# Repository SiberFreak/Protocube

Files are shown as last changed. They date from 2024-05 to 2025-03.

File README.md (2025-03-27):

# Protocube
Animation_Flourescent
Animation_Transmitted
A microscope built using 3D printed Cubes! Check out our paper!!! https://ojs.lib.uwo.ca/index.php/openhardware/article/view/22245

https://github.com/user-attachments/assets/49f3d98f-34b9-44ec-8753-2452c5d8e914

https://github.com/user-attachments/assets/b85a2b6f-8580-445c-ac9c-59f73a623541

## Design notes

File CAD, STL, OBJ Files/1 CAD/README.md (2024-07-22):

# CAD Files
Render Flourescent Upper
Render Transmitted Upper
A selection of CAD files from Autodesk Inventor Pro for everything from the cubes to tools used to assemble them.

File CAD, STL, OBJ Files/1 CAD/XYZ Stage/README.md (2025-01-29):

# XYZ Stage
Render_XYZ_Stage
An XYZ-Stage designed to use consumer electronics from Pimoroni and put them together into a functional, position control stage with an integrated LED. Currently no other attachments for the stage are available.

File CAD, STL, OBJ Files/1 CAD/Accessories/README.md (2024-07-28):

# Accessories
Render_Attatchments
A few different accessories allowing for external compatability or devices as well as some parts for light oclusion.

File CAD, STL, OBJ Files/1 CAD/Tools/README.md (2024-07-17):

# Tools
Render_Tools
A set of tools usefull for helping in the assembly of the cubes and baseplate, as well as for aligning the beam path.

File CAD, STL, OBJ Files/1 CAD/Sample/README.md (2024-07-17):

# Sample
Render_Sample
Am alternative fixed mount for a sample plate.

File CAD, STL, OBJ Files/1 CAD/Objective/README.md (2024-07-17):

# Objective
Render_Objective
A Pink cube designed to hold a standard microscope objective. It is placed at the appropriate distance on the z-axis for use with a stage.

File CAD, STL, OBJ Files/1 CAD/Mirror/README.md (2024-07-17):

# Mirrors
Render_Mirror_Horizontal
Render_Mirror_Vertical
Purple cubes designed to fit a rectangular mirror. The mirror’s distance and alignment are determined by three brass thread inserts heat pressed in, along with an M3 Screw contacting magnets on the mirror plate.

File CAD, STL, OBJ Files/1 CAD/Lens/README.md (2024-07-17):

# Lenses
Render_Lens_One_Inch
Render_Lens_Half_Inch
Light Blue Cubes designed to hold a standard 1” and 1/2" optical lens, the lens is fixed in place by an M4 set screw and a press fit cap for extra security. The lens is aligned positionally by two M6 set screws and a manual rail adjustment.

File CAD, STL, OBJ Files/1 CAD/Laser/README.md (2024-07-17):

# Laser
Render_Light_Source
A White cube that holds the light source and is adjustable in the same way as the lenses, but with two mounts to align and tilt the light source. It also includes covers to be enclosed once aligned.

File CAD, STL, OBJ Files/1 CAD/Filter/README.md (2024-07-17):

# Filters
Render_Filter
A few different ways of mounting filts, both to the cubes and the usb lasers.

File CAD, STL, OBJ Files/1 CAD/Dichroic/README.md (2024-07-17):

# Dichroic
Render_Dichroic
A Yellow cube designed to hold a standard 1” Dichroic. It is sized for SM1 to hold standard 1” filters via press fit.

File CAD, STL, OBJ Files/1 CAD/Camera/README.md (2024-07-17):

# Camera
Render_Camera
A Red cube designed to fit a standard size SM1 via a press fit and keep the light path enclosed.

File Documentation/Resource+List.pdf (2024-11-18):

Part | Description | Weight(g, ml) | CostPerUnit | Amount | Price | Link

Printed Parts (Cubes)

Cube V5 (Slotted) | N/A | 23.6 | $0.71 | 6 | $4.26 | Github (https://github.com/Siber18/Protocube/tree/main)
Cube V5 (Closed) | N/A | 26.94 | $0.81 | 23 | $18.63 | Github (https://github.com/Siber18/Protocube/tree/main)
Cube V5 (Mixed) | N/A | 22.11 | $0.66 | 2 | $1.32 | Github (https://github.com/Siber18/Protocube/tree/main)
Cube V5 | N/A | 18.06 | $0.54 | 2 | $1.08 | Github (https://github.com/Siber18/Protocube/tree/main)

Printed Parts (Inserts)

Dichroic Mirror Mount | N/A | 23.37 | $0.70 | 1 | $0.70 | Github (https://github.com/Siber18/Protocube/tree/main)
Filter Mount SM1 | N/A | 4.44 | $0.13 | 1 | $0.13 | Github (https://github.com/Siber18/Protocube/tree/main)
Filter Mount SM05 | N/A | 5.64 | $0.17 | 0 | $0.00 | Github (https://github.com/Siber18/Protocube/tree/main)
Half Inch Lense Holder | N/A | 4.62 | $0.14 | 1 | $0.14 | Github (https://github.com/Siber18/Protocube/tree/main)
One Inch Lense Holder | N/A | 5.86 | $0.18 | 3 | $0.54 | Github (https://github.com/Siber18/Protocube/tree/main)
One Inch Lense Holder (SM1) | N/A | 6.32 | $0.19 | 0 | $0.00 | Github (https://github.com/Siber18/Protocube/tree/main)
One Inch Lense Holder (SM05) | N/A | 4.52 | $0.14 | 0 | $0.00 | Github (https://github.com/Siber18/Protocube/tree/main)
Laser Mount (USB Laser) | N/A | 5.21 | $0.16 | 2 | $0.32 | Github (https://github.com/Siber18/Protocube/tree/main)
Laser Mount (Smaller Laser) | N/A | 4.70 | $0.14 | 0 | $0.00 | Github (https://github.com/Siber18/Protocube/tree/main)
Mirror Base Horizontal | N/A | 9.43 | $0.28 | 2 | $0.56 | Github (https://github.com/Siber18/Protocube/tree/main)
Mirror Plate Horizontal | N/A | 4.23 | $0.13 | 2 | $0.26 | Github (https://github.com/Siber18/Protocube/tree/main)
Mirror Base Vertical | N/A | 13.50 | $0.41 | 1 | $0.41 | Github (https://github.com/Siber18/Protocube/tree/main)
Mirror Plate Vertical | N/A | 3.56 | $0.11 | 1 | $0.11 | Github (https://github.com/Siber18/Protocube/tree/main)
Flashlight Mount | N/A | 14.68 | $0.44 | 1 | $0.44 | Github (https://github.com/Siber18/Protocube/tree/main)
Objective Mount | N/A | 13.12 | $0.39 | 1 | $0.39 | Github (https://github.com/Siber18/Protocube/tree/main)
Tunnel Horizontal | N/A | 21.17 | $0.64 | 1 | $0.64 | Github (https://github.com/Siber18/Protocube/tree/main)
Tunnel Vertical | N/A | 14.49 | $0.43 | 1 | $0.43 | Github (https://github.com/Siber18/Protocube/tree/main)

Printed Parts (XYZ Stage)

X Stage Body | N/A | 5.71 | $0.17 | 1 | $0.17 | Github (https://github.com/Siber18/Protocube/tree/main)
XStage Clamp | N/A | 1.29 | $0.04 | 1 | $0.04 | Github (https://github.com/Siber18/Protocube/tree/main)
X Stage Motor Clamp | N/A | 0.91 | $0.03 | 1 | $0.03 | Github (https://github.com/Siber18/Protocube/tree/main)
X Stage Part | N/A | 6.86 | $0.21 | 1 | $0.21 | Github (https://github.com/Siber18/Protocube/tree/main)
Y Stage Body | N/A | 10.81 | $0.32 | 1 | $0.32 | Github (https://github.com/Siber18/Protocube/tree/main)
Y Stage Motor Clamp | N/A | 1.2 | $0.04 | 1 | $0.04 | Github (https://github.com/Siber18/Protocube/tree/main)
Y Stage Part | N/A | 3.02 | $0.09 | 1 | $0.09 | Github (https://github.com/Siber18/Protocube/tree/main)
Z Stage Body | N/A | 63.58 | $1.91 | 1 | $1.91 | Github (https://github.com/Siber18/Protocube/tree/main)
Z Stage Electrical Cover | N/A | 4.07 | $0.12 | 1 | $0.12 | Github (https://github.com/Siber18/Protocube/tree/main)
Z Stage LED Mount | N/A | 1.13 | $0.03 | 1 | $0.03 | Github (https://github.com/Siber18/Protocube/tree/main)
Z Stage Motor Clamp | N/A | 1.08 | $0.03 | 1 | $0.03 | Github (https://github.com/Siber18/Protocube/tree/main)
Z Stage Part | N/A | 20.34 | $0.61 | 1 | $0.61 | Github (https://github.com/Siber18/Protocube/tree/main)
Joystick Lower Mount | N/A | 3.72 | $0.41 | 1 | $0.41 | Github (https://github.com/Siber18/Protocube/tree/main)
Joystick Upper Mount | N/A | 2.58 | $0.08 | 1 | $0.08 | Github (https://github.com/Siber18/Protocube/tree/main)

Printed Parts (Tools)

Baseplate Magnet Press | N/A | 32.62 | $0.98 | 1 | $0.98 | Github (https://github.com/Siber18/Protocube/tree/main)
Bottom Cube Press | N/A | 6.01 | $0.18 | 1 | $0.18 | Github (https://github.com/Siber18/Protocube/tree/main)
Top Cube Press | N/A | 6.01 | $0.18 | 1 | $0.18 | Github (https://github.com/Siber18/Protocube/tree/main)
Laser Alignment Tool | N/A | 3.27 | $0.10 | 25 | $2.50 | Github (https://github.com/Siber18/Protocube/tree/main)

Parts List (McMaster)

Multipurpose 304 Stainless Steel Rod | 3mm x 3ft | N/A | $9.42 | 1 | $9.42 | https://www.mcmaster.com/1272T33-1272T12/
Alloy Steel Low-Profile Socket Head Screw | M3 x 0.5 mm Thread, 12 mm Long 25ct | N/A | $7.85 | 1 | $7.85 | https://www.mcmaster.com/93070A070/
Black-Oxide Alloy Steel Socket Head Screw | M3 x 0.5 mm Thread, 8 mm Long, 100ct | N/A | $9.22 | 1 | $9.22 | https://www.mcmaster.com/91290A113/

Parts List (Thorlabs)

Optical Adhesive | Bonding Glass to Plastic | N/A | $40.70 | 1 | $40.70 | https://www.thorlabs.com/thorproduct.cfm?partnumber=NOA68
F30 1/2" Lense | 1/2" Lense | N/A | $60.59 | 1 | $60.59 | https://www.thorlabs.com/thorproduct.cfm?partnumber=AC127-030-A
F200 1" Lense | 1" Lense | N/A | $89.10 | 3 | $267.30 | https://www.thorlabs.com/thorproduct.cfm?partnumber=AC254-200-A
M4 x 5mm Setscrew | 50ct | N/A | $5.90 | 1 | $5.90 | https://www.thorlabs.com/thorproduct.cfm?partnumber=SS4MS5
M6 x 12mm Secrew | 25ct | N/A | $6.43 | 1 | $6.43 | https://www.thorlabs.com/thorproduct.cfm?partnumber=SS6MS10
M6 x 16mm Setscrew | 25ct | N/A | $6.97 | 1 | $6.97 | https://www.thorlabs.com/thorproduct.cfm?partnumber=SS6MS16

Parts List (Amazon)

Magnets 4mm | 200ct | N/A | $9.99 | 5 | $49.95 | https://a.co/d/f4sNGOT
Magnets 5mm | 150ct | N/A | $9.99 | 1 | $9.99 | https://a.co/d/0iCdR7lo
M3 x 0.5-Pitch Length Coupling Nuts | 8mm | N/A | $7.39 | 1 | $7.39 | https://a.co/d/6JjM6d4
Knurled Threaded Insert | M3 x 5mm L x 4mm OD, 100ct | N/A | $8.50 | 1 | $8.50 | https://a.co/d/bxMPw1L
Motor Gearboxes | DC 6V Gear Motor | N/A | $8.61 | 3 | $25.83 | https://a.co/d/5GOWpqV
Mini USB Cable | For Camera | N/A | $5.99 | 1 | $5.99 | https://a.co/d/7T3tGII
Super Glue | You will need it | N/A | $9.99 | 1 | $9.99 | https://a.co/d/7T3tGII
Hot Glue Gun | You will need it | N/A | $18.97 | 1 | $18.97 | https://a.co/d/0bAOghhe
USB-C Cables x 2 | For XYZ Stage | N/A | $5.99 | 1 | $5.99 | https://a.co/d/i5DBRwO
Stainless Steel Rods | For XYZ Stage | N/A | $7.99 | 0.25 | $2.00 | https://a.co/d/hvkBlIS

Parts List (Adafruit)

Gamepad | Mini I2C Gamepad with seesaw - STEMMA QT / Qwiic | N/A | $7.50 | 1 | $7.50 | https://www.adafruit.com/product/5743
Adafruit LED Sequins | Warm White | N/A | $3.95 | 1 | $3.95 | https://www.adafruit.com/product/1758

Parts List (DigiKey)

STEMMA QT/QWIIC CABLE | 400mm | N/A | $1.50 | 1 | $1.50 | https://www.digikey.com/en/products/detail/adafruit-industries-llc/5385/16546436
QUAD MOTOR CONTROLLER | MOTOR 2040 | N/A | $24.60 | 1 | $24.60 | https://www.digikey.com/en/products/detail/pimoroni-ltd/PIM618/17051430

Parts List (Pimoroni)

JST-SH Cables x 4 | 300mm | N/A | $4.90 | 1 | $4.90 | https://shop.pimoroni.com/products/jst-sh-cable-6-pin?variant=39292536488019
Encoder Kits | Micro Metal Motor Encoder (MMME) (pack of 2) | N/A | $9.42 | 1 | $9.42 | https://shop.pimoroni.com/products/micro-metal-motor-encoder?variant=39888423321683
Encoder Kits (Sideways) | Micro Metal Motor Encoder (MMME) (pack of 2) | N/A | $9.42 | 1 | $9.42 | https://shop.pimoroni.com/products/micro-metal-motor-encoder?variant=39888423354451
Motors | Micro Metal Gearmotor (Extended back shaft) – 50:1 | N/A | $4.82 | 3 | $14.46 | https://shop.pimoroni.com/products/micro-metal-gearmotor-extended-back-shaft?variant=3073681025
QUAD MOTOR CONTROLLER | MOTOR 2040 | N/A | $30.00 | 1 | $30.00 | https://shop.pimoroni.com/products/motor-2040?variant=39884997853267

Parts List (Misc)

Barrel Jack Switch | For any other lasers | N/A | $2.75 | 1 | $2.75 | https://www.sparkfun.com/products/11705
Heat Set Insert Kit | M3 Heat Inserts | N/A | $9.89 | 1 | $9.89 | https://west3d.com/products/heat-insert-tool-kit
White Acrylic (Standard) | Opaque, Glossy, Masked, Cast, 1/8" | N/A | $18.50 | 1 | $18.50 | https://shop.glowforge.com/products/white-acrylic-cast-opaque-glossy?variant=39434530783330
Laptop | Gateway 11.6" Ultra Slim Notebook | N/A | $89.00 | 1 | $89.00 | Gateway 11.6" Ultra Slim Notebook, HD, Intel® Celeron®, Dual Core, 64GB Storage, 4GB RAM, Mini HDMI, 1.0MP Webcam, Windows 10 S (https://www.walmart.com/ip/Gateway-11-6-Ultra-Slim-Notebook-HD-Intel-Celeron-Dual-Core-64GB-Storage-4GB-RAM-Mini-HDMI-1-0MP-Webcam-Windows-10-S-Microsoft-365-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)
Prusament PLA | One for Each Color + 3 Blacks | 1000g | $30.00 | 12 | $360.00 | https://www.prusa3d.com/category/prusament-pla/
Bambu Labs PLA-CF | 1kg | 1000g | $34.99 | 1 | $34.99 | https://us.store.bambulab.com/products/pla-cf?variant=41003202248840
Bambu Lab A1 Printer Bundle | Recommended Printer | N/A | $1,449.00 | 1 | $1,449.00 | https://us.store.bambulab.com/collections/3d-printer/products/a1

Mirrors

Plane Mirror General Purpose | 40x25x3mm | N/A | 20.57 | 3 | $61.71 | https://www.knightoptical.com/stock/plane-mirror-f-s-general-purpose-40x25x3mmthk-enhanced-aluminium-visible-use.html

Lasers (Choose One)

Red Laser | 650nm | N/A | $9.98 | 1 | $9.98 | https://a.co/d/3TRZW0U
Blue Laser | 405nm | N/A | $17.98 | 1 | $17.98 | https://a.co/d/7nuj360
Green Laser | 532nm | N/A | $9.98 | 1 | $9.98 | https://a.co/d/a5kr8Kf

Cameras (Choose One)

DMK 22BUC03

The Imaging Source “One for all” camera, USB 2.0, 1/3“ CMOS, monochrome, max resolution 744x480, ROI to increase speed, global shutter, trigger in, digital out, C/CS-mount (Without lens and cables)

N/A | $206.00 | 1 | $206.00 | https://dl-gui.theimagingsource.com/en_US/0ea79de3-100f-510e-8601-2ba7061b001e/

DMK 42BUC03

The Imaging Source “One for all” camera, USB 2.0, 1/3“ CMOS, monochrome, 1280x960 pixel, global shutter, trigger in, digital out, C/CS-mount, WITHOUT lens and cables

N/A | $229.00 | 1 | $229.00 | https://www.theimagingsource.com/en-us/product/industrial/2u/dmk42buc03/

Objectives (Choose One)

20x Microscope Objective Lens | CCIS EC Plan 20x Strain Free Microscope Objective Lens | N/A | $317.00 | 1 | $317.00 | https://www.motic-microscope.com/p-763-ccis-ec-plan-20x-strain-free-microscope-objective-lens.aspx
40x Microscope Objective Lens | CCIS EC Plan 40x Strain Free Microscope Objective Lens | N/A | $414.00 | 1 | $414.00 | https://www.motic-microscope.com/p-1846-ccis-ec-plan-40x-strain-free-microscope-objective-lens.aspx

Dichroics & Filters (Choose One)

Custom_405LaserSetZET405/10xT4 | Chroma ID: CS451075, Containing zet405/10x, T425LPXR-UF1 and ET460/50m,25mm diameter excitation/clean-up and barrier/emissionfilters, 25.5x36x1mm thick dichroic mirror | N/A | $825.00 | 1 | $825.00 | N/A

Custom_532LaserSetZET532/10xZT

Chroma ID: CS451193, Containing zet532/10x, zt532rdc-UF1 and ET575/50m,25mm diameter excitation/clean-up and barrier/emissionfilters, 25.5x36x1mm thick dichroic mirror

N/A | $825.00 | 1 | $825.00 | N/A

Custom_640LaserSetZET640/20xZT

Chroma ID: CS451194, Containing zet640/20x, zt640rdc-UF1 and ET690/50m,25mm diameter excitation/clean-up and barrier/emissionfilters, 25.5x36x1mm thick dichroic mirror

N/A | $825.00 | 1 | $825.00 | N/A

## Total

$2,765.84

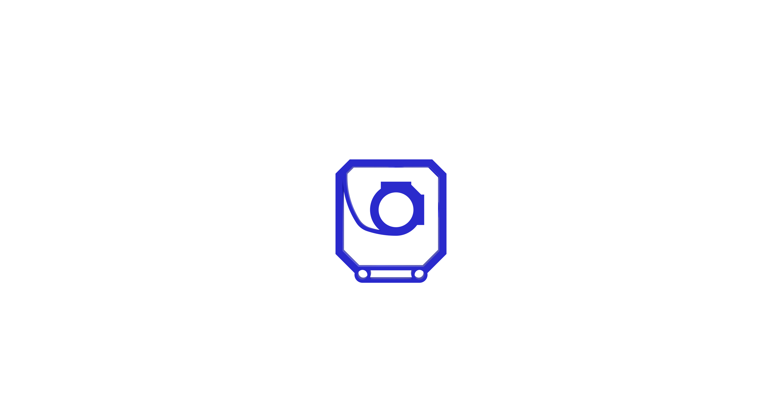
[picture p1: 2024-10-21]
Resources/Renders/Basic_Renders/Render_Lens_Mount_Half_Inch.png

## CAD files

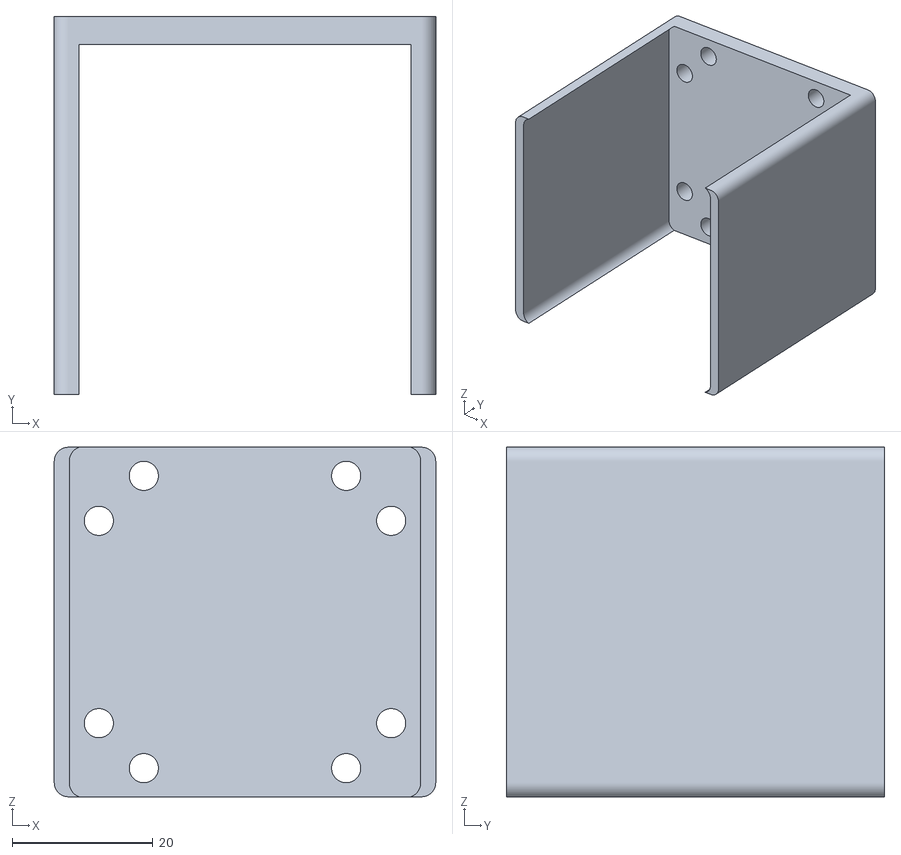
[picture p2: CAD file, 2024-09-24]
CAD, STL, OBJ Files/2 STL/V5_Outer Cover Full_61.stl
54.3 x 53.8 x 49.8

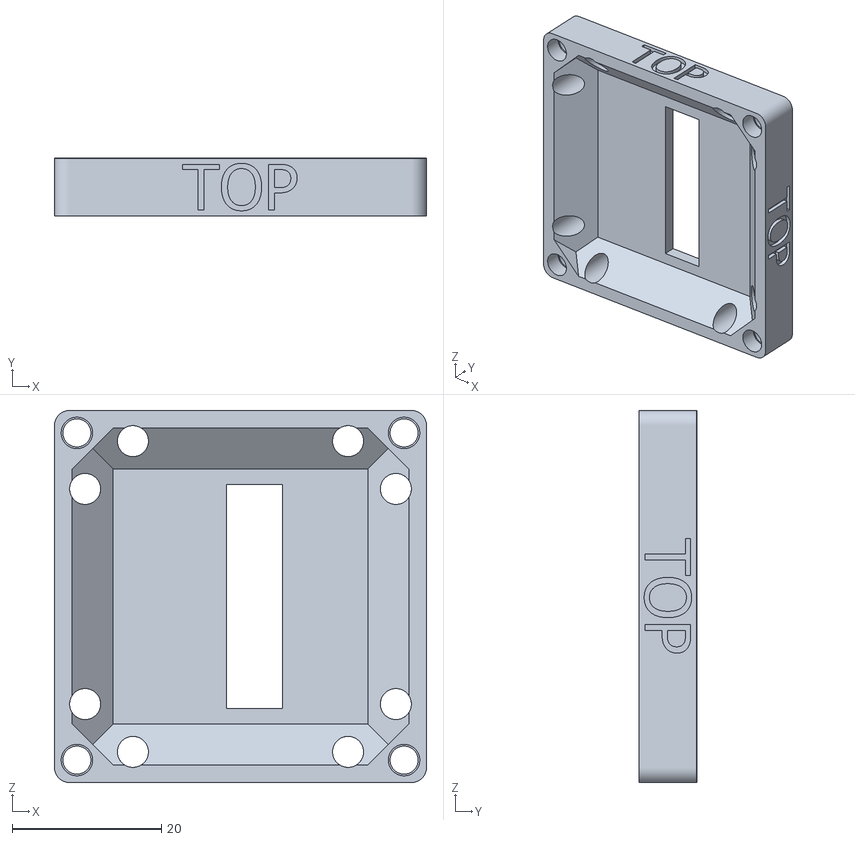
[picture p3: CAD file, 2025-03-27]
CAD, STL, OBJ Files/2 STL/V5_Cube 1x1 Top V5 Closed Slotted_5.stl
49.8 x 7.70 x 49.8

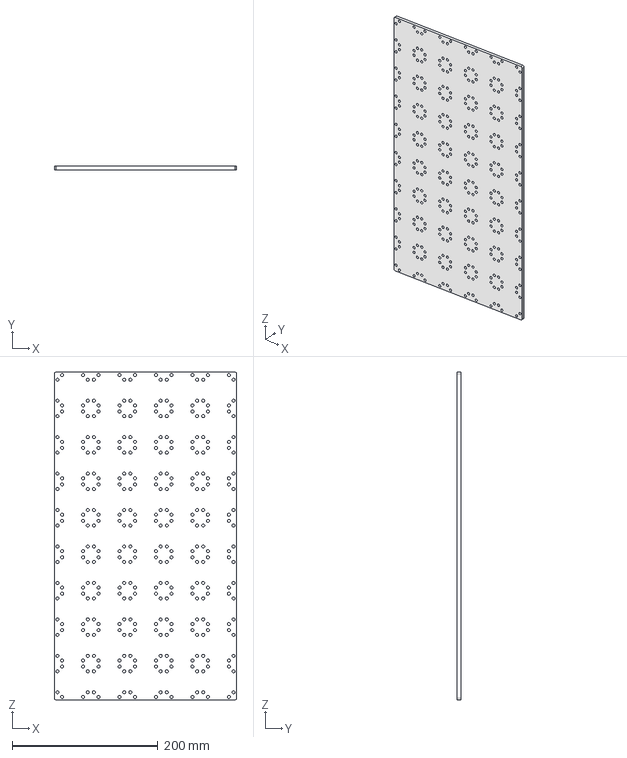
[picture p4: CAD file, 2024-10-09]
CAD, STL, OBJ Files/4 STEP/Baseplate 9x5 V5.stp
250.0 x 5.00 x 450.0 mm

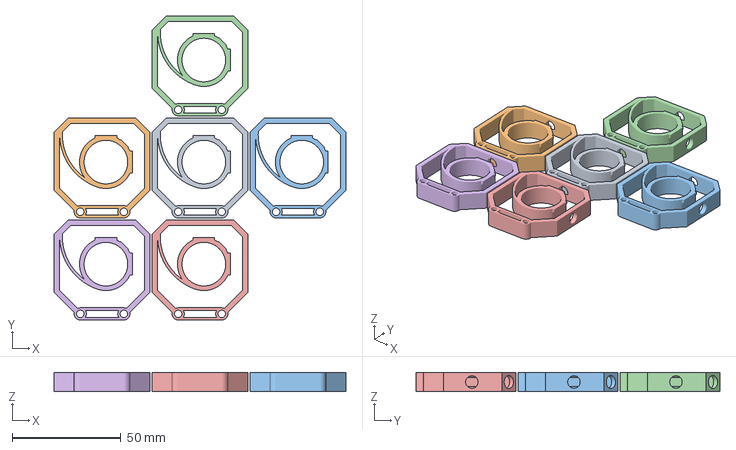
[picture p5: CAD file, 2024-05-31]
Resources/Slicer Files/Laser Holders.3mf
133.8 x 139.5 x 8.75 mm
Cube 1x1 V5_Laser Holder (USB Laser)_22.stl x 6

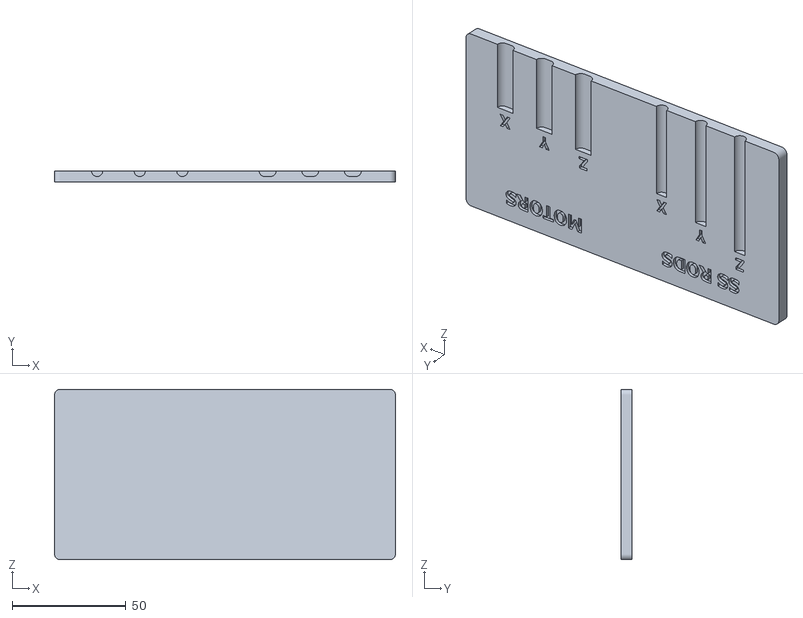
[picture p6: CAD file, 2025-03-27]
CAD, STL, OBJ Files/2 STL/V5_Rod_Motor_Lengths_15.stl
150.0 x 5.00 x 75.0

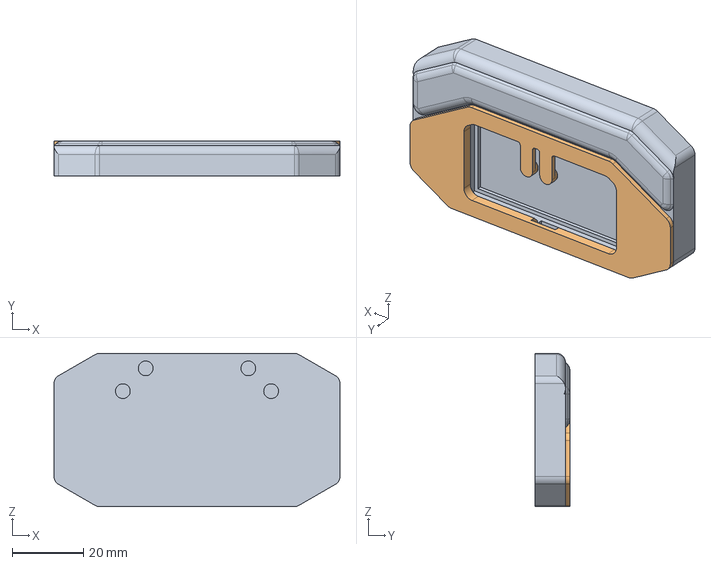
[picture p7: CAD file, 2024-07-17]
CAD, STL, OBJ Files/4 STEP/Gamepad Enclosure.stp
80.2 x 9.75 x 43.0 mm
Joystick Bottom
Joystick Top

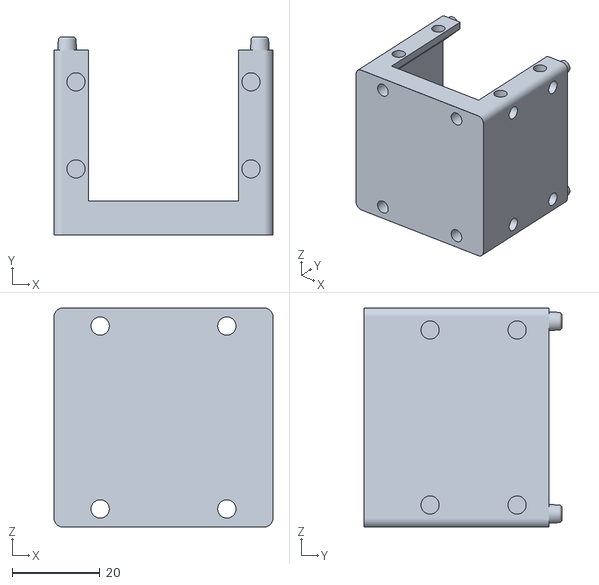
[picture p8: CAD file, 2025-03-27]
CAD, STL, OBJ Files/2 STL/V5_Cube 1x1 Bottom V5 Closed_4.stl
49.8 x 45.0 x 49.8

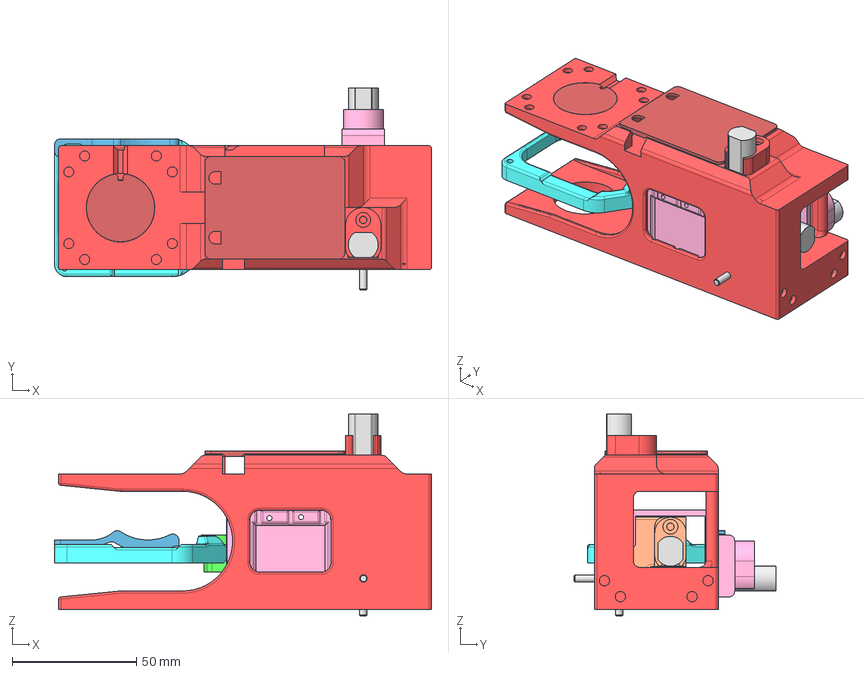
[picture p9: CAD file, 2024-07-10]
CAD, STL, OBJ Files/4 STEP/XYZ Stage V5.stp
151.4 x 81.0 x 81.0 mm
DC Motor x 3
Z Stage Body New
Z Stage Part V5
Z Stage LED Mount V5
Z Stage Electrical Cover
Z Stage Motor Clamp V5
Y Stage Body v5
Y Stage Part V5
Y Stage Motor Clamp V5
X Stage Body V5
X Stage Part V5
X Stage Clamp V5
X Stage Motor Clamp V5

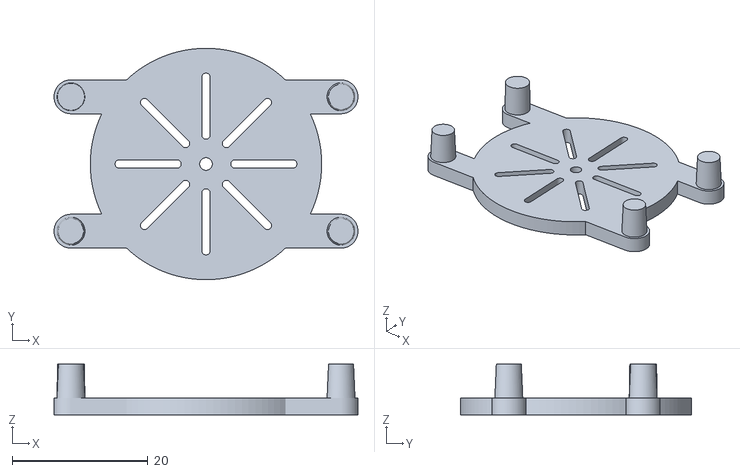
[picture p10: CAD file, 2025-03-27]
CAD, STL, OBJ Files/2 STL/V5_Laser Alignment Tool V1_9.stl
44.8 x 34.1 x 7.50

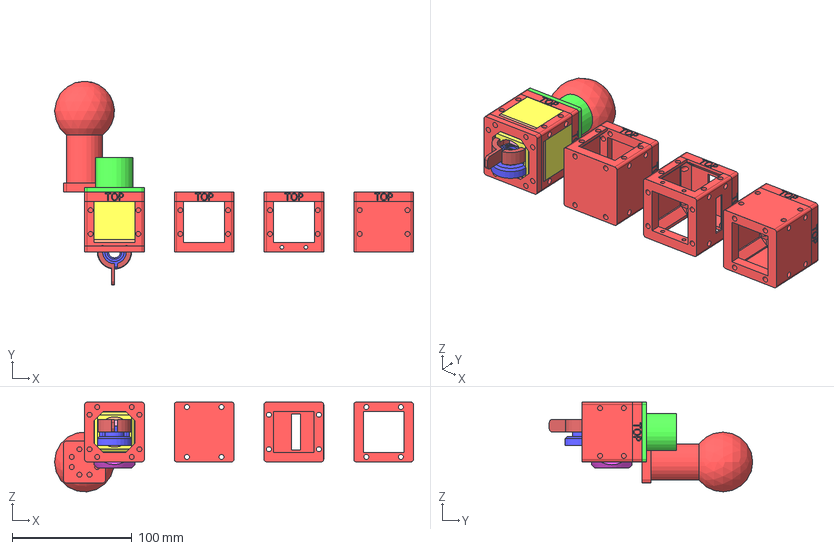
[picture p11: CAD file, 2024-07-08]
CAD, STL, OBJ Files/4 STEP/Cube 1x1 V5.stp
299.3 x 169.7 x 74.8 mm
Cube 1x1 Top V5 x 2
Cube 1x1 Bottom V5
Cube 1x1 Top V5 Closed
Cube 1x1 Bottom V5 Closed
Cube 1x1 Top V5 Closed Slotted Rails
Cube 1x1 Bottom V5 Closed Slotted Rails
Cube 1x1 Bottom V5 Closed Vertical
Laser Alignment Tool V1
Laser Alignment Tool V2
Cube Press Top
Cube 1x1 V5 Bot Press
Cube 1x1 V5 Press
Laser Switch
Half Inch Lense Holder Cover (V5)
One Inch Lense Holder Cover (V5)
Half Inch Lense Holder (V5)
One Inch Lense Holder (V5)
Laser Holder (USB)
Laser Holder (Blue Laser)
SM05 Lense Holder (V5)
Special One Inch Lense Holder (V5)
Filter Mount (SM1)
Filter Mount (SM1)_1
Mirror Base
Mirror Plate
Mirror Base Horizontal
Mirror Plate Horizontal
Dichroic Mirror Mount (V2)
Camera Mount Side
Objective Mount
Filter Adapter (SM1)
Filter Adapter (SM05)
Camera Mount Top
Top Mount (SM05)
Flashlight Mount V1
Cover Side (Normal) Proto
Cover Side (Slotted) Proto

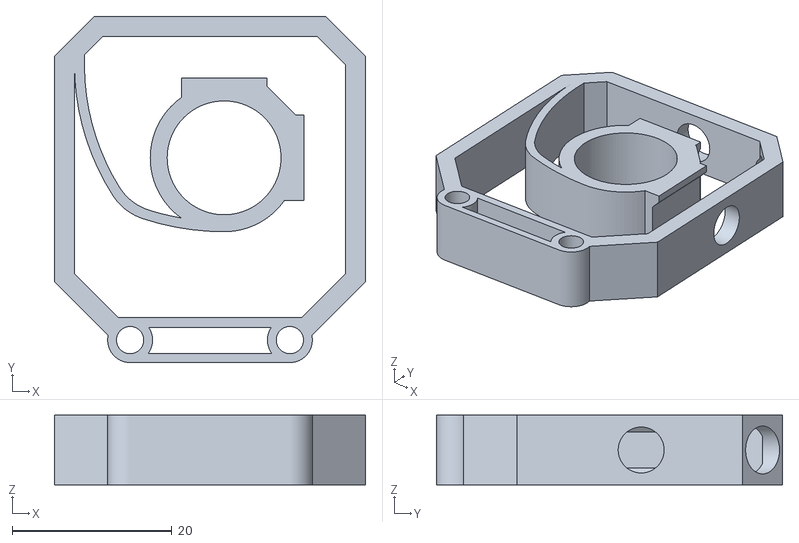
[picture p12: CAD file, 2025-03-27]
CAD, STL, OBJ Files/2 STL/V5_Laser Holder (Battery Laser)_29.stl
38.9 x 43.3 x 8.75

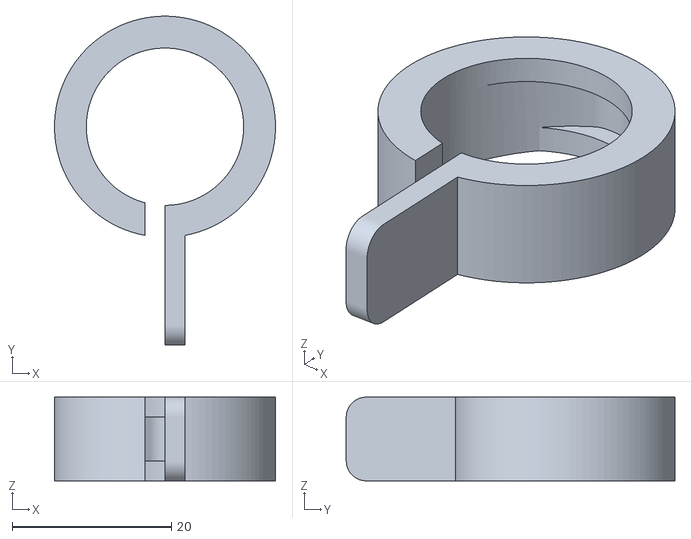
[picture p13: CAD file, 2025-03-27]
CAD, STL, OBJ Files/2 STL/V5_Laser Switch (USB Laser)_20.stl
27.7 x 41.2 x 10.5

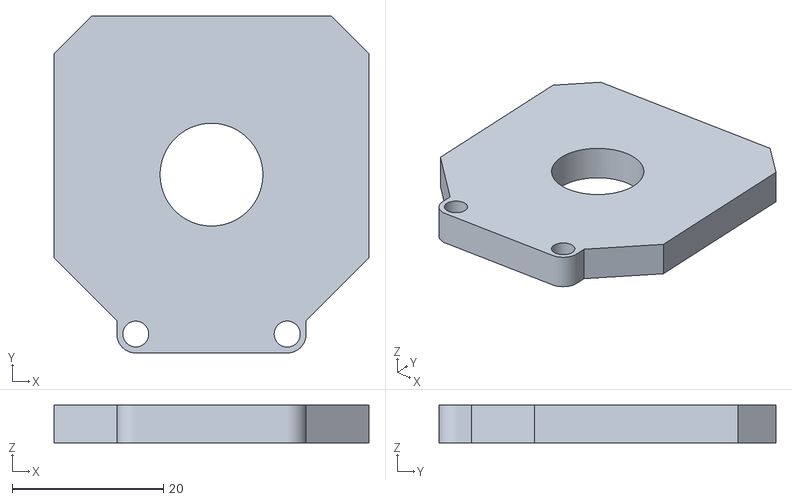
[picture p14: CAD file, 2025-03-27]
CAD, STL, OBJ Files/2 STL/V5_Filter Mount (SM05)_27.stl
41.6 x 44.5 x 5.00

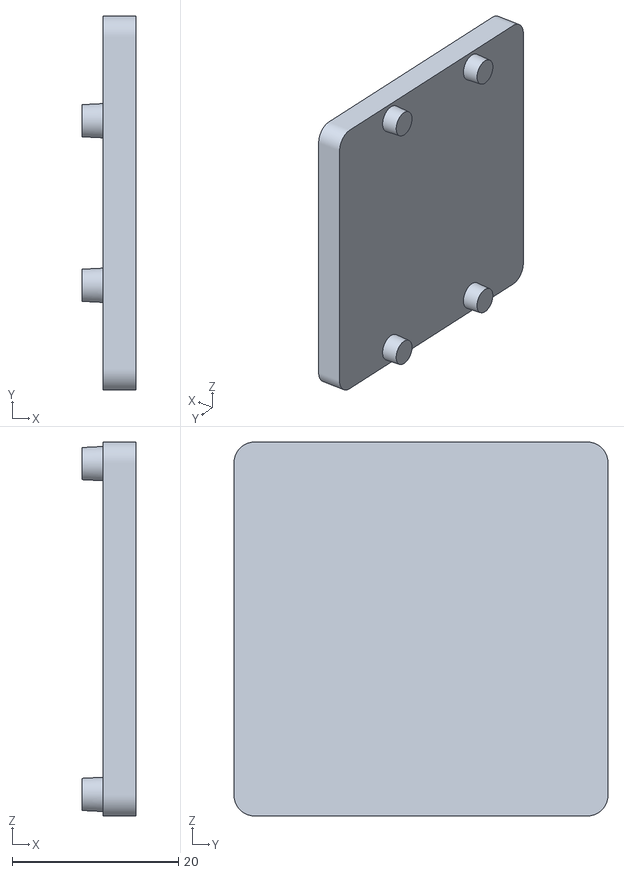
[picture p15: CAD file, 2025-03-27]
CAD, STL, OBJ Files/2 STL/V5_Outer Cover Side_56.stl
6.50 x 45.0 x 45.0

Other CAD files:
CAD, STL, OBJ Files/2 STL/V5_Laser Switch (Battery Laser)_19.stl
CAD, STL, OBJ Files/2 STL/V5_Outer Cover Side Open_55.stl
CAD, STL, OBJ Files/2 STL/V5_Laser Holder (Smaller)_31.stl
CAD, STL, OBJ Files/2 STL/V5_Cube 1x1 Bottom V5 Closed Vertical_8.stl
CAD, STL, OBJ Files/1 CAD/Accessories/Flashlight Mount V1.ipt
CAD, STL, OBJ Files/1 CAD/Accessories/Mounting Bar.ipt
CAD, STL, OBJ Files/1 CAD/Accessories/Top Mount (SM05).ipt
CAD, STL, OBJ Files/1 CAD/Accessories/Top Mount (SM1).ipt
CAD, STL, OBJ Files/1 CAD/Accessories/Tunnel Horizontal.ipt
CAD, STL, OBJ Files/1 CAD/Accessories/Tunnel Vertical.ipt
CAD, STL, OBJ Files/1 CAD/Baseplates/Baseplate 9x5 V5.ipt
CAD, STL, OBJ Files/1 CAD/Baseplates/Interlinking Baseplate Pathed Angle V1.ipt
CAD, STL, OBJ Files/1 CAD/Baseplates/Interlinking Baseplate Pathed Angle V2.ipt
CAD, STL, OBJ Files/1 CAD/Baseplates/Interlinking Baseplate Pathed Female.ipt
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

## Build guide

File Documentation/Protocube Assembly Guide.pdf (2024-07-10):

# Assembly/Manufacturing Guide

- Tool Manufacturing
- The tools are printed on a Voron 2.4R2 (https://vorondesign.com/voron2.4) with a StealthBurner Extruder, (https://vorondesign.com/voron_stealthburner) using these (https://drive.google.com/file/d/10SKDTJkAxmJ7EOjJHBFUqbAFyTCSYFc9/view?usp=drive_link) print settings in PrusaSlicer and glue from a BambuLab glue stick (https://us.store.bambulab.com/products/glue-stick-for-build-plate) to hold the parts in place.
■ Use Prusament PLA (https://www.prusa3d.com/en/product/prusament-pla-jet-black-1kg/) as the source material for the printer.
■ The print settings should be set to “0.2mm 0.4nozzle V2 - Revo”
■ For any printer questions the documentation can all be found here. (https://docs.vorondesign.com/)
- Remove the tools and clean the glue off the surface by running them under water and rubbing the surface.
■ Note: The glue also comes off easily if bathed in a warm water solution containing dish soap with some passive movement.
- Dry the tools with a paper towel or any other method.
- Insert the 4mm x 2mm Magnets (https://a.co/d/f4sNGOT) into the tools via a press fit using any sort of pliers or adjustable wrench for leverage.
■ Note: Make sure that the Top Magnet Tool has its magnets orientated to clamp onto the Bottom Magnet Tool. To ensure the cubes snap together correctly on top of each other. The Baseplate Magnet Tool should also be able to clamp onto the Bottom Magnet Tool.
- Cube Manufacturing
- The cubes are printed on a Voron 2.4R2 (https://vorondesign.com/voron2.4) with a StealthBurner Extruder, (https://vorondesign.com/voron_stealthburner) using these (https://drive.google.com/file/d/10SKDTJkAxmJ7EOjJHBFUqbAFyTCSYFc9/view?usp=drive_link) print settings in PrusaSlicer and glue from a BambuLab glue stick (https://us.store.bambulab.com/products/glue-stick-for-build-plate) to hold the parts in place.
■ Use Prusament PLA (https://www.prusa3d.com/en/category/pla/) as the source material for the printer.
■ The print settings should be set to “0.2mm 0.4nozzle V2 - Revo”
■ For any printer questions the documentation can all be found here. (https://docs.vorondesign.com/)
- Remove the cubes and clean the glue off the surface by running them under water and rubbing the surface.
■ Note: The glue also comes off easily if bathed in a water solution containing dish soap and with passive movement.
- Dry the cubes with a paper towel or any other method.
- Insert the 4mm x 2mm Magnets (https://a.co/d/f4sNGOT) into the cubes via a press fit using the top and bottom magnet tools.
■ Note: The top piece will use the Top Magnet Tool, and the bottom piece will use the Bottom Magnet Tool.
- Inserts and Other Parts
- All other parts and inserts are printed using a BambuLab X1-C, (https://us.store.bambulab.com/collections/3d-printer/products/x1-carbon-combo) using just the default print settings, with slight adjustments here and there to enable support for overhanging surfaces.
■ Print using official BambuLab Glue Sticks (https://us.store.bambulab.com/products/glue-stick-for-build-plate) and a Smooth Plate. (https://us.store.bambulab.com/collections/bambu-build-plates/products/bambu-smooth-pei-plate)
■ Everything but the lens and laser mounts should be printed in Prusament PLA, (https://www.prusa3d.com/en/product/prusament-pla-jet-black-1kg/) the lens and laser mounts are printed in PLA-CF. (https://us.store.bambulab.com/products/pla-cf?variant=41003202248840)

- Lens Assembly
- Grab a closed-slotted cube, a correctly sized lens mount, and, if you are not using an SM1 or SM05 mount, its corresponding cover.
- Cut two 3mm Stainless Steel Rods (https://www.mcmaster.com/1272T33-1272T12/) to a length of 48mm, and grab two M6 set screws (https://www.thorlabs.com/thorproduct.cfm?partnumber=SS6MS16) of appropriate lengths, and one M4 set screw. (https://www.thorlabs.com/thorproduct.cfm?partnumber=SS4MS5)
- Insert the two M6 set screws into the lens mount into the two holes on the side and top.
- If you are not using an SM1 or SM05 mount, insert the lens with its direction facing forward towards the smaller diameter of the lens mount.
■ Insert the M4 set screw into the small hole on the top right of the lens mount and tighten only until the lens does not move anymore, do not overtighten!
- If you are using an SM1 or SM05 mount, press fit the lens into the corresponding mount.
- Insert the Lense Assembly into the cube, with the set screw on the side poking out of the slot on the cube, and tap fit the two 3mm rods into place with a rubber mallet.
- Fasten the top piece of the cube into the correct spot corresponding to the set screws and the ability to slide the lens back and forth.
- Laser Assembly
- Grab a closed slotted bottom cube piece and a normal top cube piece, whichever laser mount works for your laser source, if need be also include the laser switch for the USB lasers, and whichever corresponding ND filter mount works as well; with the adapters being used with the USB laser sources, and the regular mounts being used for other laser sources.
- Cut two 3mm Stainless Steel Rods (https://www.mcmaster.com/1272T33-1272T12/) to a length of 98mm, and grab four M6 set screws (https://www.thorlabs.com/thorproduct.cfm?partnumber=SS6MS16) of appropriate lengths, and two M4 set screws. (https://www.thorlabs.com/thorproduct.cfm?partnumber=SS4MS5)
- Insert the two M6 set screws into the laser mounts into the two holes on the side and top.
- Insert the Laser Mounts into the cubes, with the set screw on the side poking out of the slot on the cube, and tap fit the two 3mm rods into place with a rubber mallet.
- Insert the laser so that it is within both laser mounts, and if necessary, also include the laser switch for the USB lasers, and fasten it into place using the two M4 set screws on the laser mounting points, do not overtighten!
- Fasten the top pieces of the cubes into the correct spot corresponding to the set screws and the ability to slide the laser back and forth.
- Vertical Mirror Assembly
- Grab a normal cube, a vertical mirror base, a vertical mirror plate, as well as three M3 Knurled Inserts, (https://a.co/d/0dgLV4en) three ferrous M3 Screws, (https://www.mcmaster.com/91290A113/) and three 5mm Magnets. (https://a.co/d/0iCdR7lo)

- Heat-press the three knurled inserts into the three corresponding holes on the base piece using a soldering iron attachment. (https://west3d.com/products/heat-insert-tool-kit)
- Press-fit the three magnets into the plate, and then glue a 30mm x 40mm optical mirror surface to the other side of the plate.
- Screw the three screws into the inserts and attach the plate to the ends of the screws using the magnets.
- Slide the assembly into the bottom cube piece and attach the top cube piece.
- Horizontal Mirror Assembly
- Grab a normal bottom cube piece and a closed top cube piece, a horizontal mirror base, a horizontal mirror plate, as well as three M3 Knurled Inserts, (https://a.co/d/0dgLV4en) three ferrous M3 Screws, (https://www.mcmaster.com/91290A113/) and three 5mm Magnets. (https://a.co/d/0iCdR7lo)
- Heat-press the three knurled inserts into the three corresponding holes on the base piece using a soldering iron attachment. (https://west3d.com/products/heat-insert-tool-kit)
- Press-fit the three magnets into the plate, and then glue a 30mm x 47.5mm optical mirror surface to the other side of the plate.
- Screw the three screws into the inserts and attach the plate to the ends of the screws using the magnets.
- Slide the assembly into the bottom cube piece and attach the top cube piece.
- Dichroic Assembly
- Grab a normal cube, a dichroic mount, an appropriate 25.5mm x 36mm x 1mm dichroic mirror, and appropriate 1” filters.
- Slot the 25.5mm x 36mm x 1mm dichroic mirror into the corresponding slot.
- Insert a standard SM1 clip and an appropriate 1” Filter into both circular holes, and then clamp them into place with another SM1 clip.
- Camera Assembly
- Grab a normal cube and a camera mount.
- Insert the camera mount into the bottom cube piece.
- Attach the top cube piece.
- Objective Assembly
- Grab a normal cube, and an objective mount.
- Insert the objective mount into the bottom cube piece.
- Attach the top cube piece.
- XYZ Stage Assembly
- Joystick Assembly

■ Grab the two printed joystick pieces, as well as an Adafruit Gamepad, (https://www.adafruit.com/product/5743) a QT/QWIIC Cable, (https://www.digikey.com/en/products/detail/adafruit-industries-llc/5385/16546436) and four 4mm x 2mm Magnets. (https://a.co/d/f4sNGOT)

■ Press-fit the magnets into the Joystick Base using the Bottom Magnet Tool.
■ Insert the Gamepad into the bottom piece, with the connector at the back facing the opening.
■ Place a dab of hot glue on the very edge of the corners of the gamepad and press the top piece into place.
- Note: Take care not to get any hot glue on the joystick or buttons. ■ Pull the top piece off of the joystick, put a tiny amount of hot glue in the hole on the top piece, and press fit it back onto the joystick.
- Note: Take care not to let any hot glue drip onto the lower joystick assembly.
■ Insert the QT/QWIIC cable into its port, and place a few more dabs of hot glue to hold it in place.
- Stage Assembly

■ Preparation
- Grab the printed pieces from the xyz stage, four 2mm Stainless Steel Rods, (https://a.co/d/hvkBlIS) three M3 x 8mm nuts, (https://a.co/d/6JjM6d4) thirty-six 4mm x 2mm Magnets, (https://a.co/d/f4sNGOT) three DC Motors with Screws, (https://a.co/d/5GOWpqV) three DC Motors with Extended Backs, (https://shop.pimoroni.com/products/micro-metal-gearmotor-extended-back-shaft?variant=3073681025) two Sideways Encoders, (https://shop.pimoroni.com/products/micro-metal-motor-encoder?variant=39888423354451) one Normal Encoder, (https://shop.pimoroni.com/products/micro-metal-motor-encoder?variant=39888423321683) eight Low Profile M3 Screws, (https://www.mcmaster.com/93070A070/) one Controller Board, (https://shop.pimoroni.com/products/motor-2040?variant=39884997853267) four JST-SH Cables, (https://shop.pimoroni.com/products/jst-sh-cable-6-pin?variant=39292536455251) and an Adafruit LED Sequin. (https://www.adafruit.com/product/1758)
■ Rods
- Safely cut the stainless-steel rods into the following lengths.
- Six 48.7mm Z Axis
- Six 44mm Y Axis
- Six 39mm X Axis
■ Motors
- Safely cut the M3 screw rods to the following lengths from the flat surface of the gearbox assembly.
- One 36.5mm X Axis
- One 34.5mm Y Axis
- One 25.5mm Z Axis
- Unscrew the gearboxes from both sets of motors and take something like a wire stripper to clamp onto and remove the gears from the shaft of each motor.
- Note: Keep track of what gear they are, and which motor they are from and be careful not to damage them.
- Assemble the M3 gear and gearbox onto the motor with the extended back shaft, press fitting the gear on and then screwing the gearbox back on.
- Note: Careful not to strip the screws, they are very tiny.

- On the Y Axis and Z Axis Motors, solder on the sideways encoder kits.
- Note: Make sure that the polarities on the motor and circuit board are aligned.
- On the X Axis Motor, solder on the normal encoder kit.
- Note: Make sure that the polarities on the motor and circuit board are aligned.
- Press fit the encoder wheel onto the shaft with the dots facing away from the motor, ensuring there is less than a 2mm gap between it and the hall-effect sensors on the board.
■ Motor 2040
- Take the Motor 2040 board, and while holding the Boot/User button plug it into a pc, a device should show up in file explorer.
- Drop this UF2 file (https://github.com/Siber18/Protocube/blob/main/Resources/Circuit%20Python/adafruit-circuitpython-pimoroni_motor2040-en_US-9.0.5.uf2) into the device and keep it plugged in, this will install circuit python onto the board.
- Once it is installed a device called Circuit Python will show up, and you should copy paste these library files (https://github.com/Siber18/Protocube/blob/main/Resources/Circuit%20Python/lib.zip) into the “lib” folder.
- It will have a file named code.py, open this file with Notepad++, and copy paste this code (https://github.com/Siber18/Protocube/blob/main/Resources/Circuit%20Python/XYZ%20Stage%20Code.py) over any currently existing code, and save the file.
- The device will reconnect, and you should see the motor lights indicating they are trying to move, this will happen with or without motors connected.
■ Adafruit Sequin LED
- Take the Adafruit LED and one of the JST-SH cables, plug the JST-SH cable into the Motor 2040, on the cable, cut off the other end as far as you can, and then cut the four wires to the right on the motor 2040 end, leaving the two wires on the left.
- Note: These are the motor power connections, they will be used to power the LED.
- Solder the right wire, or the one on the inside, to the negative terminal on the LED, and the left wire, or the one on the outside, to the positive terminal on the LED.
- Note: Make sure the led side is facing towards the wires, so that the empty spot with the resistor is facing away from the wires.

■ Assembly
- Press-fit the M3 nuts into the side slot on the X Stage Body, Y Stage Body, and Z Stage Part, and secure them in place with a light layer of hot glue on top of them.
- Press-fit four magnets into the Z Stage Body on the back using the Top Magnet Tool.

- Press-fit eight magnets into the top of the Z Stage Body using the Top Magnet Tool, and the other twenty-four magnets to the bottom using the Bottom Magnet Tool
■ X Axis
- Grab the X Stage Body and Y Stage Part, and slot the X Body through the Y Part
- Note: The two flat sides should be facing towards each other.
- Grab the X Stage Part and slot it into the square receptacle on the X Stage Body.
- Note: The larger radius on the X Body should be fitted into the slot on the top of the X Part.
- Secure the two x stage parts together with one of the low profile M3 screws, do not overtighten!
- Grab two X Stage Clamps and screw them into the X Part where the two holes are, they will hold your sample plate in place, do not overtighten!
- Insert the six 39.8mm rods into the Y Stage Body and slide the X Stage Body through them so that the two holes on either part line up.
- Press-fit the Y Stage Part onto the rails and secure it into place with two low profile M3 screws.
■ X Motor
- Temporarily hook up the X Axis Motor to the D Spot on the Motor 2040 using a JST-SH cable and plug the joystick’s cable into the QW/ST port.
- Note: Make sure you are plugging in the cables correctly or you will damage the pins.
- Plug in the Motor 2040 to a USB outlet and it will spin the motor in the direction required to screw it into place, making sure to align the motor so that the encoder port points away from the main X/Y Bodies, and let it screw itself all the way in.
- Grab the X Motor Clamp and attach it to the motor, making sure to line up the holes and inset for the screw head.
- Secure the motor in place with another low profile M3 screw and disconnect the JST-SH cable from the motor and disconnect the Motor 2040 from USB power.
■ Y Axis
- Grab the Z Stage Part and insert the assembly so that the M3 nut on the assembly and the corresponding motor mount line up.
- Insert the six 44mm steel rods into the side of the Z Part, making sure that they pass through the Y Body correctly and are flush with the other side of the Z Part.
■ Y Motor

- Temporarily hook up the Y Axis Motor to the D Spot on the Motor 2040 using a JST-SH cable
- Note: Make sure you are plugging in the cables correctly or you will damage the pins.
- Plug in the Motor 2040 to a USB outlet and it will spin the motor in the direction required to screw it into place, make sure to align the motor so that the encoder port points towards the X Axis Sample Clamps, and let it screw itself all the way in.
- Grab the Y Motor Clamp and attach it to the motor, making sure to line up the holes and inset for the screw head.
- Secure the motor in place with another low profile M3 screw and disconnect the JST-SH cable from the motor and disconnect the Motor 2040 from USB power.
■ Z Axis
- Grab the Z Stage Body and insert the assembly so that the M3 nut on the assembly and the corresponding motor mount line up.
- Insert the six 48.7mm steel rods into the bottom of the Z Body, making sure that they pass through the Z Part correctly and that they are fully inserted and not sticking out from the bottom.
- Note: You may need to use some force from a mallet to tap them into place fully. Make sure to be gentle though as you can split your printed part with too much force, if necessary, use one of the magnet tools for the cubes to support the edge.
■ Z Motor
- Temporarily hook up the Z Axis Motor to the D Spot on the Motor 2040 using a JST-SH cable.
- Note: Make sure you are plugging in the cables correctly or you will damage the pins.
- Plug in the Motor 2040 to a USB outlet and it will spin the motor in the direction required to screw it into place, make sure to align the motor so that the encoder port points towards the X Axis Sample Clamps, and let it screw itself all the way in.
- Grab the Z Motor Clamp and attach it to the motor, making sure to line up the holes and inset for the screw head.
- Secure the motor in place with another low profile M3 screw and disconnect the JST-SH cable from the motor and disconnect the Motor 2040 from USB power.
- Electronics Assembly
■ Motor 2040
- Grab the Motor 2040 with the LED plugged into port A on the board and mount it to the top of the Z Axis Body using a dab of hot glue in each corner.

- Note: The USB-C port and other corresponding ports will line up where you should place the board.
■ Adafruit Sequin LED
- Mount the LED to the Z Stage LED Mount using hot glue to hold it in place to the recess on the underside with the wires being hot glued there as well.
- Mount the LED Mount to the stage making sure to line up the wires with the channel on the top.
- Note: The hot glue gun will melt the wire’s insulation away, so be careful to only let the hot glue touch them.
- Mount the wires into the recessed channel that runs to the motor 2040, leaving some slack on the Motor 2040 side.
- Note: The hot glue gun will melt the wire’s insulation away, so be careful to only let the hot glue touch them.
■ Motors
- Connect the X Axis Motor to the D Port on the Motor 2040 using a JST-SH Cable, and then put a dab of hot glue on both connections to secure them in place.
- Connect the Y Axis Motor to the C Port on the Motor 2040 using a JST-SH Cable, and then put a dab of hot glue on both connections to secure them in place.
- Connect the Z Axis Motor to the B Port on the Motor 2040 using a JST-SH Cable, and then put a dab of hot glue on both connections to secure them in place.
■ As a finishing touch, attach the Electronics Cover to the stage above the Motor 2040 using a dollop of hot glue in each corner, and then press fitting it into the correct direction and orientation.

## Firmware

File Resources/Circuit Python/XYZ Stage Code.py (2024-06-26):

# SPDX-FileCopyrightText: 2021 ladyada for Adafruit Industries
# SPDX-FileCopyrightText: 2023 Kattni Rembor for Adafruit Industries

# SPDX-License-Identifier: MIT

import time
import board
import pwmio
import digitalio
import rotaryio
from digitalio import DigitalInOut, Direction
from analogio import AnalogIn
from adafruit_motor import motor

from micropython import const
from adafruit_seesaw.seesaw import Seesaw


addr0_pin = DigitalInOut(board.ADC_ADDR_0)
addr0_pin.direction = Direction.OUTPUT

addr1_pin = DigitalInOut(board.ADC_ADDR_1)
addr1_pin.direction = Direction.OUTPUT

addr2_pin = DigitalInOut(board.ADC_ADDR_2)
addr2_pin.direction = Direction.OUTPUT

analog_in = AnalogIn(board.SHARED_ADC)


def get_voltage(pin):
    return (pin.value * 3.3) / 65536


def select(address):
    addr0_pin.value = address & 0b001
    addr1_pin.value = address & 0b010
    addr2_pin.value = address & 0b100

# Motor constants
FREQUENCY = 25000               # Chose a frequency above human hearing
DECAY_MODE = motor.SLOW_DECAY   # The decay mode affects how the motor
# responds, with SLOW_DECAY having improved spin
# threshold and speed-to-throttle linearity

# Create the pwm objects
pwm_a_p = pwmio.PWMOut(board.MOTOR_A_P, frequency=FREQUENCY)
pwm_a_n = pwmio.PWMOut(board.MOTOR_A_N, frequency=FREQUENCY)
pwm_b_p = pwmio.PWMOut(board.MOTOR_B_P, frequency=FREQUENCY)
pwm_b_n = pwmio.PWMOut(board.MOTOR_B_N, frequency=FREQUENCY)
pwm_c_p = pwmio.PWMOut(board.MOTOR_C_P, frequency=FREQUENCY)
pwm_c_n = pwmio.PWMOut(board.MOTOR_C_N, frequency=FREQUENCY)
pwm_d_p = pwmio.PWMOut(board.MOTOR_D_P, frequency=FREQUENCY)
pwm_d_n = pwmio.PWMOut(board.MOTOR_D_N, frequency=FREQUENCY)

# Create the motor objects
mot_a = motor.DCMotor(pwm_a_p, pwm_a_n)
mot_b = motor.DCMotor(pwm_b_p, pwm_b_n)
mot_c = motor.DCMotor(pwm_c_p, pwm_c_n)
mot_d = motor.DCMotor(pwm_d_p, pwm_d_n)
motors = [mot_a, mot_b, mot_c, mot_d]

# Set the motor decay modes (if unset the default will be FAST_DECAY)
mot_a.decay_mode = DECAY_MODE
mot_b.decay_mode = DECAY_MODE
mot_c.decay_mode = DECAY_MODE
mot_d.decay_mode = DECAY_MODE

# Create the encoder objects
enc_a = rotaryio.IncrementalEncoder(board.ENCODER_A_B, board.ENCODER_A_A, divisor=1)
enc_b = rotaryio.IncrementalEncoder(board.ENCODER_B_B, board.ENCODER_B_A, divisor=1)
enc_c = rotaryio.IncrementalEncoder(board.ENCODER_C_B, board.ENCODER_C_A, divisor=1)
enc_d = rotaryio.IncrementalEncoder(board.ENCODER_D_B, board.ENCODER_D_A, divisor=1)
encoders = [enc_a, enc_b, enc_c, enc_d]

BUTTON_X = const(6)
BUTTON_Y = const(2)
BUTTON_A = const(5)
BUTTON_B = const(1)
BUTTON_SELECT = const(0)
BUTTON_START = const(16)
button_mask = const(
    (1 << BUTTON_X)
    | (1 << BUTTON_Y)
    | (1 << BUTTON_A)
    | (1 << BUTTON_B)
    | (1 << BUTTON_SELECT)
    | (1 << BUTTON_START)
)

Joy_X = const(14)
Joy_Y = const(15)
last_x = 0
last_y = 0
Joy_High = 675
Joy_Low = 375

i2c_bus = board.STEMMA_I2C()  # The built-in STEMMA QT connector on the microcontroller
# i2c_bus = board.I2C()  # Uses board.SCL and board.SDA. Use with breadboard.

seesaw = Seesaw(i2c_bus, addr=0x50)

seesaw.pin_mode_bulk(button_mask, seesaw.INPUT_PULLUP)

Motor_Speed = 0.275
Motor_Retract_Speed = 1.0
Motor_Retract_Timing = 3.75

Motor_Home_Check = False
LightSwitch = False
ZSwitch = False

ZPosMoveFlag = False
ZNegMoveFlag = False
YPosMoveFlag = False
YNegMoveFlag = False
XPosMoveFlag = False
XNegMoveFlag = False


VOLTAGE_GAIN = 13.9 / 3.9
CURRENT_GAIN = 1 / 0.47
CURRENT_OFFSET = -0.005
CURRENT_THRESHOLD_GLOBAL = 0.425

Encoder_Threshold_X = 32500
Encoder_Threshold_Y = 32500
Encoder_Threshold_Z = 18750
Encoder_Threshold_Global = 0

current_list = [0, 0, 0, 0]
function_current_list = [0, 0, 0, 0]

def Read_Current():
    # Read the current sense and print the values
    function_current_list = []
    for i in range(board.NUM_MOTORS):
        select(i + board.CURRENT_SENSE_A_ADDR)
        current = (get_voltage(analog_in) + CURRENT_OFFSET) * CURRENT_GAIN
        function_current_list.append(current)
        print("C", i + 1, " = ", round(current, 4), sep="", end=", ")
    print()
    return function_current_list

def Motor_Home():
    homes = [1, 2, 3]
    for i in homes:
        current_list = [0, 0, 0, 0]
        motors[i].throttle = -1.0
        time.sleep(0.75)
        while (current_list[i] < 0.175):
            time.sleep(0.1)
            current_list = Read_Current()
        motors[i].throttle = 0.0
        time.sleep(0.5)
        motors[i].throttle = 1.0
        time.sleep(0.875)
        motors[i].throttle = 0.0
        encoders[i].position = 0

def Motor_Pos_Movement(Motor, Encoder, CList, Speed, BoolMove, LastJoyVal, Current_Threshold, Encoder_Threshold):
    current_list = Read_Current()
    if (LastJoyVal > Joy_High and current_list[CList] < Current_Threshold and Encoder.position < Encoder_Threshold):
        # print("PosMove")
        Motor.throttle = Speed
        BoolMove = True
    elif (current_list[CList] > Current_Threshold):
        # print("PosFlag")
        Motor.throttle = 0.0
        BoolMove = False
    elif (Encoder.position > Encoder_Threshold):
        # print("PosFlag")
        Motor.throttle = 0.0
        BoolMove = False
    elif (LastJoyVal > Joy_Low):
        # print("PosStop")
        Motor.throttle = 0.0
        BoolMove = False
    time.sleep(0.01)
    return BoolMove

def Motor_Neg_Movement(Motor, Encoder, CList, Speed, BoolMove, LastJoyVal, Current_Threshold, Encoder_Threshold):
    current_list = Read_Current()
    if (LastJoyVal < Joy_Low and current_list[CList] < Current_Threshold and Encoder.position > Encoder_Threshold):
        # print("NegMove")
        Motor.throttle = Speed
        BoolMove = True
    elif (current_list[CList] > Current_Threshold):
        # print("NegFlag")
        Motor.throttle = 0.0
        BoolMove = False
    elif (Encoder.position < Encoder_Threshold):
        # print("NegFlag")
        Motor.throttle = 0.0
        BoolMove = False
    elif (LastJoyVal < Joy_High):
        # print("NegStop")
        Motor.throttle = 0.0
        BoolMove = False
    time.sleep(0.01)
    return BoolMove

while True:

    if not Motor_Home_Check:
        Motor_Home()
        Motor_Home_Check = True

    x_value = 1023 - seesaw.analog_read(Joy_X)
    y_value = 1023 - seesaw.analog_read(Joy_Y)

    if (abs(x_value - last_x) > 2) or (abs(y_value - last_y) > 2):
        last_x = x_value
        last_y = y_value
        # print("X = ", last_x, "Y = ", last_y)

    buttons = seesaw.digital_read_bulk(button_mask)

    if not buttons & (1 << BUTTON_SELECT):
        ZPosMoveFlag = False
        ZNegMoveFlag = False
        YPosMoveFlag = False
        YNegMoveFlag = False
        XPosMoveFlag = False
        XNegMoveFlag = False
        Motor_Home()

    if not buttons & (1 << BUTTON_Y):
        Motor_Speed = 0.275

    if not buttons & (1 << BUTTON_X):
        Motor_Speed = 0.625

    if not buttons & (1 << BUTTON_A):
        Motor_Speed = 1.0

    if (LightSwitch is False):
        if not buttons & (1 << BUTTON_B):
            while not buttons & (1 << BUTTON_B):
                LightSwitch = True
                mot_a.throttle = 0.5
                buttons = seesaw.digital_read_bulk(button_mask)

    if (LightSwitch is True):
        if not buttons & (1 << BUTTON_B):
            while not buttons & (1 << BUTTON_B):
                LightSwitch = False
                mot_a.throttle = 0.0
                buttons = seesaw.digital_read_bulk(button_mask)

    if (ZSwitch is False):
        if not buttons & (1 << BUTTON_START):
            while not buttons & (1 << BUTTON_START):
                ZSwitch = True
                buttons = seesaw.digital_read_bulk(button_mask)

    if (ZSwitch is True):
        if not buttons & (1 << BUTTON_START):
            while not buttons & (1 << BUTTON_START):
                ZSwitch = False
                buttons = seesaw.digital_read_bulk(button_mask)

    if (ZSwitch is False):

        if (YNegMoveFlag is False ):
            # print("PositiveYStart")
            YPosMoveFlag = Motor_Pos_Movement(mot_c, enc_c, 2, +Motor_Speed, YPosMoveFlag, last_x, CURRENT_THRESHOLD_GLOBAL, Encoder_Threshold_Y)

        if (YPosMoveFlag is False):
            # print("NegativeYStart")
            YNegMoveFlag = Motor_Neg_Movement(mot_c, enc_c, 2, -Motor_Speed, YNegMoveFlag, last_x, CURRENT_THRESHOLD_GLOBAL, Encoder_Threshold_Global)

        if (XNegMoveFlag is False):
            # print("PositiveXStart")
            XPosMoveFlag = Motor_Pos_Movement(mot_d, enc_d, 3, +Motor_Speed, XPosMoveFlag, last_y, CURRENT_THRESHOLD_GLOBAL, Encoder_Threshold_X)

        if (XPosMoveFlag is False):
            # print("NegativeXStart")
            XNegMoveFlag = Motor_Neg_Movement(mot_d, enc_d, 3, -Motor_Speed, XNegMoveFlag, last_y, CURRENT_THRESHOLD_GLOBAL, Encoder_Threshold_Global)

    if (ZSwitch is True):
        if (ZNegMoveFlag is False):
            # print("PositiveStart")
            ZPosMoveFlag = Motor_Pos_Movement(mot_b, enc_b, 1, +Motor_Speed, ZPosMoveFlag, last_y, CURRENT_THRESHOLD_GLOBAL, Encoder_Threshold_Z)

        if (ZPosMoveFlag is False):
            # print("NegativeStart")
            ZNegMoveFlag = Motor_Neg_Movement(mot_b, enc_b, 1, -Motor_Speed, ZNegMoveFlag, last_y, CURRENT_THRESHOLD_GLOBAL, Encoder_Threshold_Global)

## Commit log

2024-05-31 Initial Commit
    Initial Commit To File Structure
    [Baseplate 9x5 V5.ipt, Baseplate V5 Press.ipt, Camera Mount Adapter.ipt, Camera Mount Side.ipt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]
2024-05-31 Create XYZ Stage Code.py
2024-05-31 Update XYZ Stage Code.py
    Updated the current limit values, and added a button toggle function for a future light feature.
2024-05-31 Systematic Update
    Systematic Update to move to working directly on the file within the github to improve workflows.
    [Cube (Sample).0010.iam, Cube (Sample).iam, Cube 1x1 V5 (Camera).0008.iam, Cube 1x1 V5 (Camera).iam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]
2024-06-05 Stage Lighting Built In
    Added an adafruit led into the stage on the last motor connection available.
    [X Stage Body V5.0044.ipt, X Stage Body V5.ipt, X Stage Part V5.0020.ipt, X Stage Part V5.ipt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]
2024-06-11 Stage Updates (Tolerances)
    Updated the stage tolerances to better fit components, and added the code for the led on the stage.
    [XYZ Stage V5.0119.iam, XYZ Stage V5.0122.iam, XYZ Stage V5.iam, XYZ Stage V5_DC Motor_1.stl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]
2024-06-11 Added documentation
    Added some simple documentation and fixed a cad bug that popped up.
    [Cube 1x1 V5.0444.iam, Cube 1x1 V5.iam, Protocube.0111.iam, Protocube.iam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]
2024-06-11 Updated
    Correctly describes stage Gamepad functions
2024-06-14 Updated it all to be synchronous
    [Cube 1x1 V5.stp, Cube 1x1 V5_Cube 1x1 Bottom V5 Closed Slotted_6.stl, Cube 1x1 V5_Cube 1x1 Bottom V5 Closed_4.stl, Cube 1x1 V5_Cube 1x1 Top V5 Closed Slotted_5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]
2024-06-18 Updated local readme
    Wouldn't fetch correctly
    [Protocube.0113.iam]
2024-06-18 Updated 06/18/2024
    Tolerances and File Syncs
    [Cube 1x1 V5.0445.iam, Cube 1x1 V5.iam, Cube 1x1 V5.stp, Protocube.0114.iam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]
2024-06-18 Updated Bottom Magnet Tool
    [Cube 1x1 V5 Bot Press.0002.ipt, Cube 1x1 V5 Bot Press.ipt, Cube 1x1 V5.0445.iam, Cube 1x1 V5.0446.iam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]
2024-06-23 Encoders Implemented
    Simplified the code and implemented encoder stop limits with a single fallback current protection as well.
2024-06-25 Updated to CircuitPython 9.0.5
2024-06-27 File updates
    [Cube 1x1 Bottom V5 Closed Vertical.0002.ipt, Cube 1x1 Bottom V5 Closed Vertical.ipt, Cube 1x1 V5 (Camera).0008.iam, Cube 1x1 V5 Closed Horizontal.iam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]
2024-07-08 Updates and Adjustments
    Updated the objective mount and vertical mirror assembly.
    [Cube (Sample).0010.iam, Cube 1x1 Bottom V5 Closed Vertical.0002.ipt, Cube 1x1 V5 (Dichroic).0012.iam, Cube 1x1 V5 (Mirror Vertical).0007.iam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]
2024-07-10 Adjusted some designs
    Added some last minute changes to certain designs, the lens and laser mounts were adjsuted to work better, and the dichroic was remade to simplify the cad model.
    [Cover Side (Normal).0044.ipt, Cover Side (Normal).ipt, Cube 1x1 V5 (Dichroic).0013.iam, Cube 1x1 V5 (Dichroic).iam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]
2024-07-17 Massive Update
    Added all of the blender files and renders for future referencing. Updated docs to include renders and blow-outs of each cube in the assembly guide.
    [Cube 1x1 V5 (Dichroic).0013.iam, Cube 1x1 V5 (Dichroic).0014.iam, Cube 1x1 V5 (Dichroic).iam, Cube 1x1 V5 (USB Laser).0006.iam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]
2024-07-17 Synced the Model Exports
    Synced the exported model files to match the current CAD models.
    [Cube 1x1 V5 (Dichroic).0014.iam, Cube 1x1 V5 (Dichroic).0015.iam, Cube 1x1 V5 (Dichroic).iam, Cube 1x1 V5 (One Inch Lense).0007.iam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]
2024-07-17 Renamed folder
    [Gamepad Bottom.ipt, Gamepad Enclosure.0009.iam, Gamepad Enclosure.iam, Gamepad Top.ipt]
2024-07-17 Updated images
    [Cube 1x1 V5.0474.iam, Protocube.0123.iam]
2024-07-22 Recolored Renders
    Recolored and renamed renders to be able to be referenced in the near future.
    [Cube 1x1 V5_Laser Holder (USB Laser)_19.3mf]
2024-07-23 Big Cad Edits
    Reorganized the main cad file and assembly that houses all of the components for the microscope.
    [Baseplate V5 Press.ipt, Cover Side (Normal).0044.ipt, Cover Top (Full).ipt, Cube 1x1 V5 (Dichroic).0015.iam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]
2024-07-23 Added Interlocking Baseplates
    [Cube 1x1 Bottom V5 Closed Taller.0001.ipt, Cube 1x1 Top V5 Closed Taller.0001.ipt, Cube 1x1 Top V5 Taller.0001.ipt, Cube 1x1 V5 (Half Inch Lens).0020.iam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]
2024-07-28 More testing and Adjustments
    [Cover Top (Full).ipt, Cover Top (Normal) Proto.ipt, Cover Top (Slotted) Proto.ipt, Cube 1x1 Bottom V5 Closed Taller.0001.ipt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]
2024-07-28 Updated images to reflect current status.
2024-07-28 Updating a mistake.
    [Cube 1x1 V5 (One Inch Lens Side Cover).iam, Outer Cover Side_MIR.ipt, Protocube.0155.iam, Protocube.iam]
2024-09-24 Updated Covers, Added Rod Length Tool
    Updated lengths to be more user friendly and added a tool for said purpose, as well as adjusted the covers for the lens cubes to hold the foam down under themselves.
    [Cube 1x1 V5 (Half Inch Lens).0022.iam, Cube 1x1 V5 (Half Inch Lens).iam, Cube 1x1 V5 (Objective).0015.iam, Cube 1x1 V5 (Objective).iam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]
2024-10-09 Updated some things
    [Baseplate 9x5 V5.stp]
2024-10-21 Lots of rendering
    Looks much better now with all screws and magnets included in renders.
2025-01-08 Motor Length Fix
    Made the motors too long and adjusted accordingly, both in the manual and the CAD files
    [Cube 1x1 V5.0532.iam, Cube 1x1 V5.iam, Rod_Motor_Lengths.0005.ipt, Rod_Motor_Lengths.ipt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]
2025-03-27 Updated the naming of certain components and added new ones.
    I updated the names of the laser components since David needed me to update them for the battery laser pointers he ordered for the Germany Trip. So I made some new holders and also made a cutting ass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
    [Cube 1x1 V5.iam, Laser Holder (Battery Laser).ipt, Laser Holder (Green Laser).0014.ipt, Laser Holder (Smaller).ipt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]
2025-03-27 Docs Updated to Current Gen
